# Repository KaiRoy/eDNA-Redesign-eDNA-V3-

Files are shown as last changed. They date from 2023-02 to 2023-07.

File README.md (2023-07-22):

# eDNA Board V3.0 - A Redesign of the OPEnS Lab's eDNA Control Board
A redesign of the Main Control Board for the eDNA Sampler

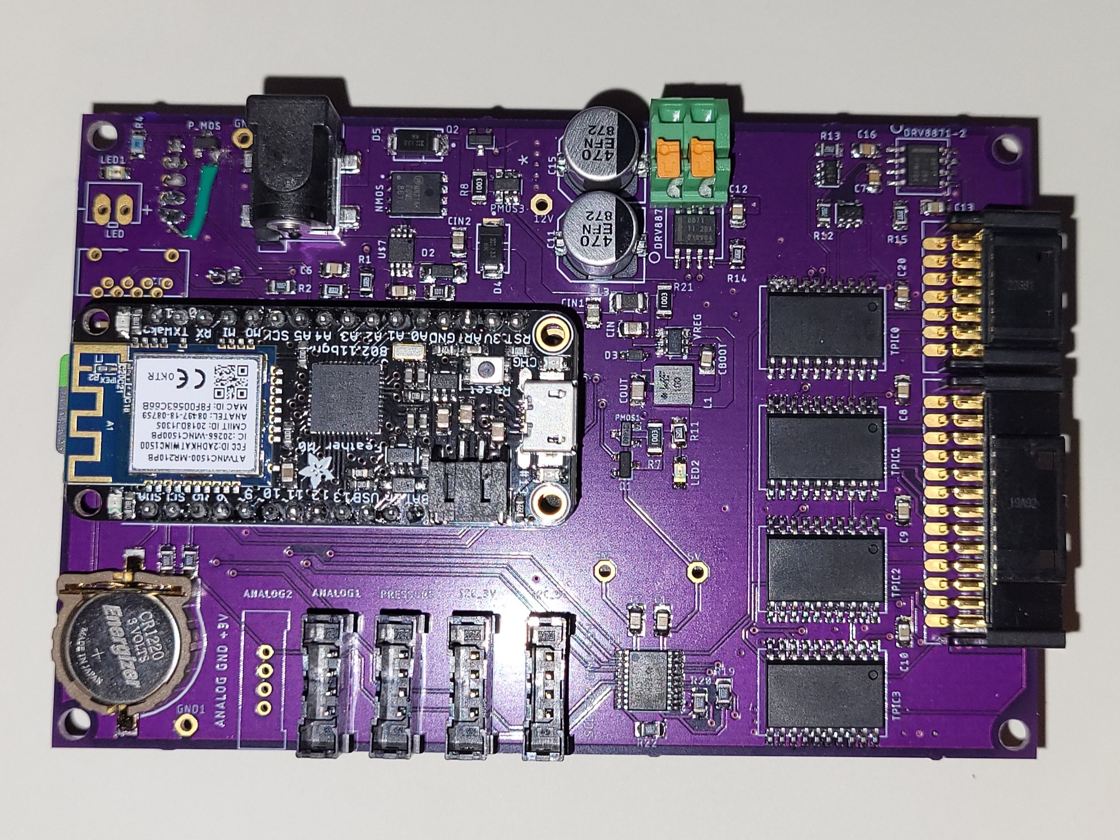
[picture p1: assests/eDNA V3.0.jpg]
Image of an assembled eDNA Board V3.0


## Table of Contents

- [Description](#description)
- [Design](#design)
- [Current State](#current-state-of-the-project)
- [Post Project Notes](#post-project-notes)
- [Installation](#installation) <!-- Should I have Installation and Usage above or below the Design, Current State, Changes, etc? -->
- [Usage](#usage)
- [Credits](#credits)
- [License](#license)

## Description

I have worked on the eDNA project at the OPEnS Lab for the past two years and during that time I noticed a couple of things that I wanted to change about the current electronics board (Dubbed eDNA Electronics V2). Because of other responsiblities, I never had the time to make those changes so I decided to make a Project Course out of it to ensure that I would have the time. This meant I had to limit the number of changes that I wanted to make for time purposes. Here were the goals for the project/redesign:
- Allowing for 5V sensor support (mainly I2C sensor support)
- Redesigning the Power Management Circuits to allow for easier integration of wake-from-sleep interrupts
- Write Documentation for this version and the previous version, since no documentation does not exist

## Designs

Most of the circuits on this board have already been designed and I had no intention of fundamentally changing them in this redesign. The circuits that are being redesigned are the sleep/power management circuit and the logic level converter circuit. The other circuits only get changed on the PCB Layout level, changing as many two-terminal components from 1206 to 0805 and general rearrangement of the PCB Layout.

![Schematic of the Power Management Circuit in eDNA Board V2]()

The power management (PM) system was designed to disable the output of the voltage regulator (Vreg). This would conserve a lot of power as most of the circuits and devices would be powered off, with only the RTC and parts of the PM circuit still functioning. This circuit work by using a D Flip Flop connected to the Microcontroller and the RTC to enable or disable the output of the Vreg Circuit. Because of this design, the microcontroller was completely off with only the RTC Interrupt able to wake up the microcontroller. This makes it difficult to add additional external interrupts to wake the system from sleep. We encountered this problem when we tried to add a button that would wake the system from sleep and trigger an operation.

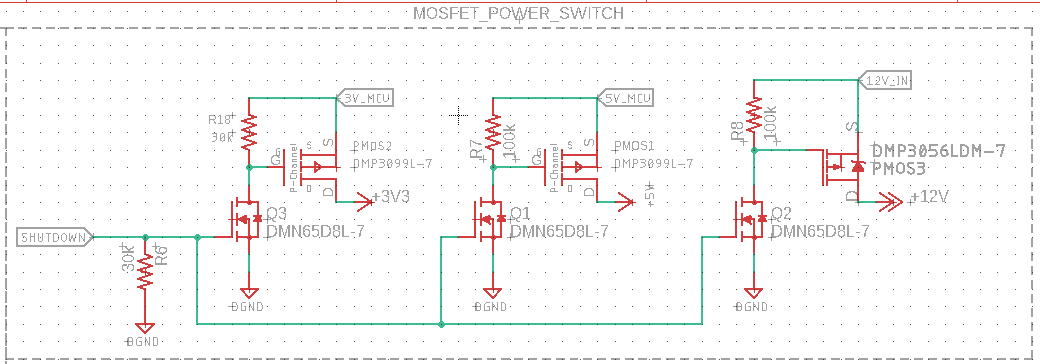
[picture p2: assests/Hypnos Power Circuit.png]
Schematic of the Power Management Circuit in Hypnosv3.4


Another project from the OPEnS Lab created a PM circuit that is used by the majority of projects at the OPEnS Lab, the eDNA project being one of the few projects that do not. This project, called the Hypnos Board, uses a series of MOSFETs to enable and disable power lines going to peripheral devices, leaving the microcontroller powered. We can further conserve power by putting the microctronller into a deep sleep. This will allow us to easily add new wake-from-sleep interrupts while still conserving power.

According to other employees at the OPEnS Lab and some online research the Adafruit Feather M0, the OPEnS Lab's Microcontroller of choice, consumes 1-2mA of current while in a software sleep. Based on the size of the battery, power consumption during operation, and the size of the battery, the approximate current draw while in sleep should be little enough that the sampler can complete a full 24 operations over the course of 30 days, which is what the eDNA Sampler was designed to be able to do. 

The change in the logic level converter circuit was needed because 5V I2C sensor support was desired for the eDNA Sampler. This is because many I2C sensors function off of 5V and limiting the system to only 3.3V I2C sensors can make it difficult to add desired features or functionality. The current logic level converter, a module from Sparkfun, only has 4-channels of conversion with three already in use. Since the circuit needed to be changed anyway, instead of using a module like the one from SparkFun, an IC was found to serve the purpose. The IC used in the v3.0 is the TXS0108E, an eight channel logic level converter.

## Current State of the Project

I was able to do some testing by the end of the term and discovered a couple of mistakes. These mistakes had to do with how I wired certain components up on at the schematic level. I misconnceted the Sleep LED and the RTC_INT Pull-Up Resistor. The sleep LED is less important but rewiring it to my always-on 3.3V line instead of my peripheral device 3.3V line allowed me to better see if the sleep switch/circuit was functioning correctly. The RTC_INT Pull-Up Resistor on the other had was a major error. I had connected the resistor to the Peripheral 3.3V line instead of the always-on 3.3V, meaning that the power would be cut during sleep. Since the RTC_INT is necessary for waking up, this caused a constant cycle of the sleep mode being enabled, the drop in voltage triggering the interrupt, the system waking up, realizing that it has not reached the desired wake-up time, and falling back asleep. 

![Image of an assembled eDNA Board V3.0 with splice wires]()

These mistakes could have been caught if I spent more time at the planning and schematic levels review the design before moving onto the PCB design. Something I plan to allocate time for in future projects. Because of this wiring issues, this version of the board remains untested. There are plans to cut the necessary traces and solder splice wires to reconenct the components and continue testing.

## Post Project Notes

In the future I would spend a lot more time verifying the schematic level of my design to ensure that I have no obvious mistakes, such as the wiring mistakes that I made in the first version of this board. If I am working on a project that is time limited, I would be sure to allocate more than enough time to spend verifying my design/schematic before moving onto the development of the PCB. 

I would also use KiCad over EAGLE in the future if possible. Having used both of the EDA softwares, I have developed a preference towards KiCad over EAGLE due to KiCad's Hotkey and Shortcut based control scheme. This has made my workflows in KiCad feel much smoother to me than my workflows in EAGLE have. In addition, I have been using the free version of EAGLE which has limitations on what can be done in the software, while KiCad does not. 

Below are a list of changes that I would recommend be made in future version of this board. I have split it into two categories as there is a difference between the changes that I would personally like to make, and the changes that I would recommend to the OPEnS Lab. Since the OPEnS Lab cannot simply make changes for the sack of making changes, the changes I recommend are ones that I see having a better Benefit-Cost Ratio conisdering the current state of the Project. 

What I would recommend for the next OPEnS Lab Version:
- Find a new Voltage Regulator IC/Redesign the Vreg Circuit
	- This IC was chosen as it had an Enable pin and its was automotive grade. Since neither of these specifications are that important I would recommend looking into a new IC that is easier to come by, since this one has been very hard to purchase in the past. 
- Redesign the Shift Registers to use the existing SPI Pins on the Feather M0
	- If that is not possible with the current Shift Registers for any reason, I would recommend finiding new Shift Registers to use in the design.

For my own personal version (outside of the OPEnS Lab):
- Switch to an ESP32 based design
	- Deep Sleep Functionality
  	- Built in RTC and WiFi Modules
  	- Similar amount of I/O Pins
	- Larger Program Memory (Our debug code is limited by the size of the Feather M0 Program Memory)
- Redesign the PCB with the intention of purchasing them preassembled. 
	- This would allow for smaller componenets to be used, components too small to be easily assembled by hand. 
	- This would allow for a two-sided PCB design i.e components on either side of the PCB, something that is hard to do by hand.

## Installation

What EDA libraries and files are needed for this project?
- eDNA Library
- Various Component Libraries
<!-- Make a singular Library for all of the components Symbols and footprints -->
<!-- Insert a link to a library guide or make my own -->

<!-- Add a link to the firmware installation guide -->
<!-- Note which code version to use -->

<!--
## Usage

Provide instructions and examples for use. Include screenshots as needed.

To add a screenshot, create an `assets/images` folder in your repository and upload your screenshot to it. Then, using the relative filepath, add it to your README using the following syntax:

    ```md
    ![alt text](assets/images/screenshot.png)
    ```

## Features

If your project has a lot of features, list them here.

## Tests

-->

## Credits

List your collaborators, if any, with links to their GitHub profiles.
- Nathan Jesudason: Modifying the [Sampler Code](https://github.com/OPEnSLab-OSU/ednaServer/tree/54-revamp-sleep-system) Changes for testing

If you used any third-party assets that require attribution, list the creators with links to their primary web presence in this section.
- OPEnS Lab's [Hypnos Board V3.4](https://github.com/OPEnSLab-OSU/OPEnS-Hypnos)
- A branch of the [ednaServer](https://github.com/OPEnSLab-OSU/ednaServer/tree/54-revamp-sleep-system) code
<!-- Link the Symbols and Footprints used? -->

## License

Licensed under the [CERN-OHL-S-2.0](LICENSE.txt) License

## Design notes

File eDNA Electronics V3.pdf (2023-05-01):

# eDNA Electronics V3

By Kai Quintin Kurisaka Roy

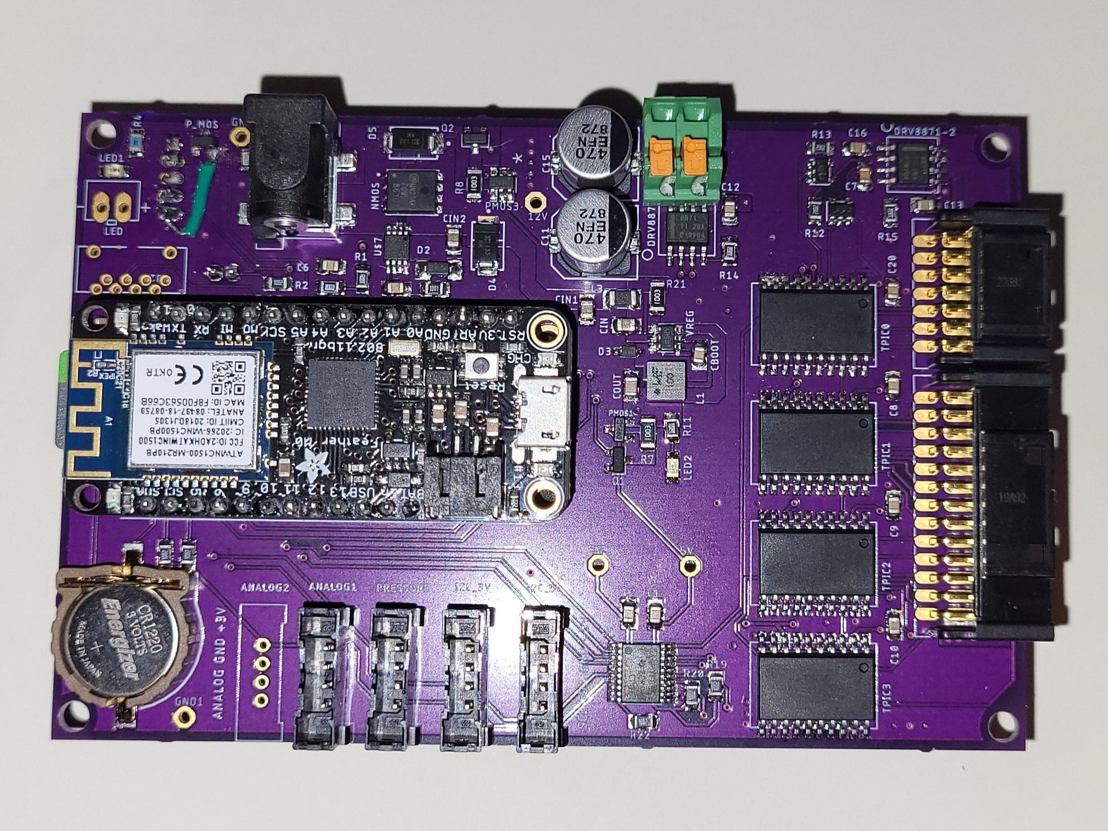
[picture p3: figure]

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
Table of Con

tents

2
Top Le

vel Block Diagrams

2
Whole Circuit Schematics and PCB

2
Micocontroller
- Adafruit

Feather M0 WiFi

2
Pin Usag

e in our Circuit:

4
R

e

verse Curren

t Protection (RCP) Circuit

7
Voltag

e

Regula

tor (VReg) Circuit

9
MOSFET

P

o

wer Control Circuit | 11
Valv
e Control Circuit: | 12
Motor/Ball

Valv

e Control Circuit: | 15
Other/Miscellaneous Circuits | 16
Sleep Mode Control Circuit: | 16
Logic Con
verter: | 18
SD Car
d Circuit: | 18
Connectors: | 18
Notes on

Possible Impr

o

vements: | 19

# Top Level Block Diagrams

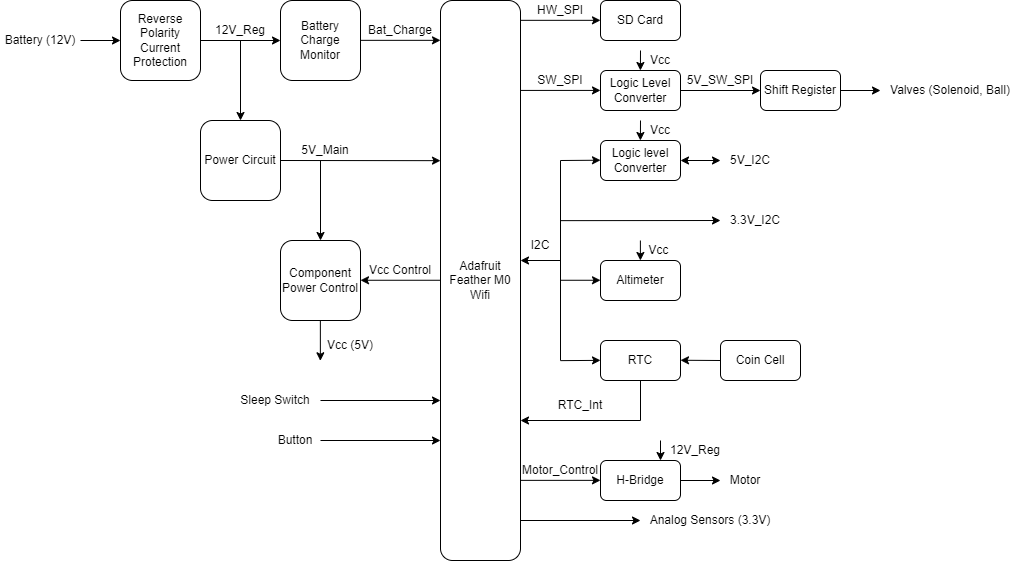
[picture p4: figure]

Figure #: Top-Level Block Diagram

# Whole Circuit Schematics and PCB

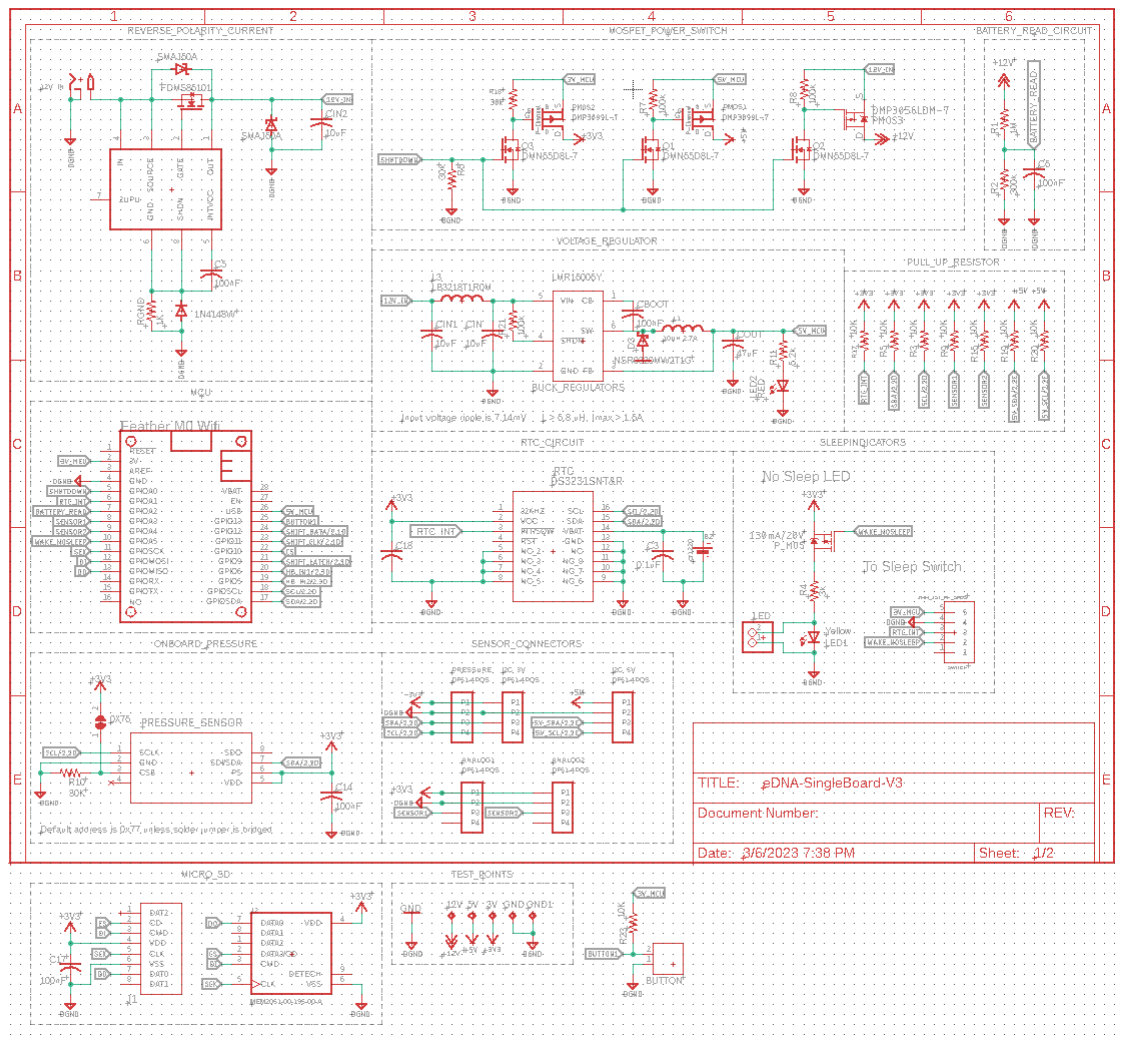
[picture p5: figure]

Figure #: Sheet 1 of the eDNA Board Schematic

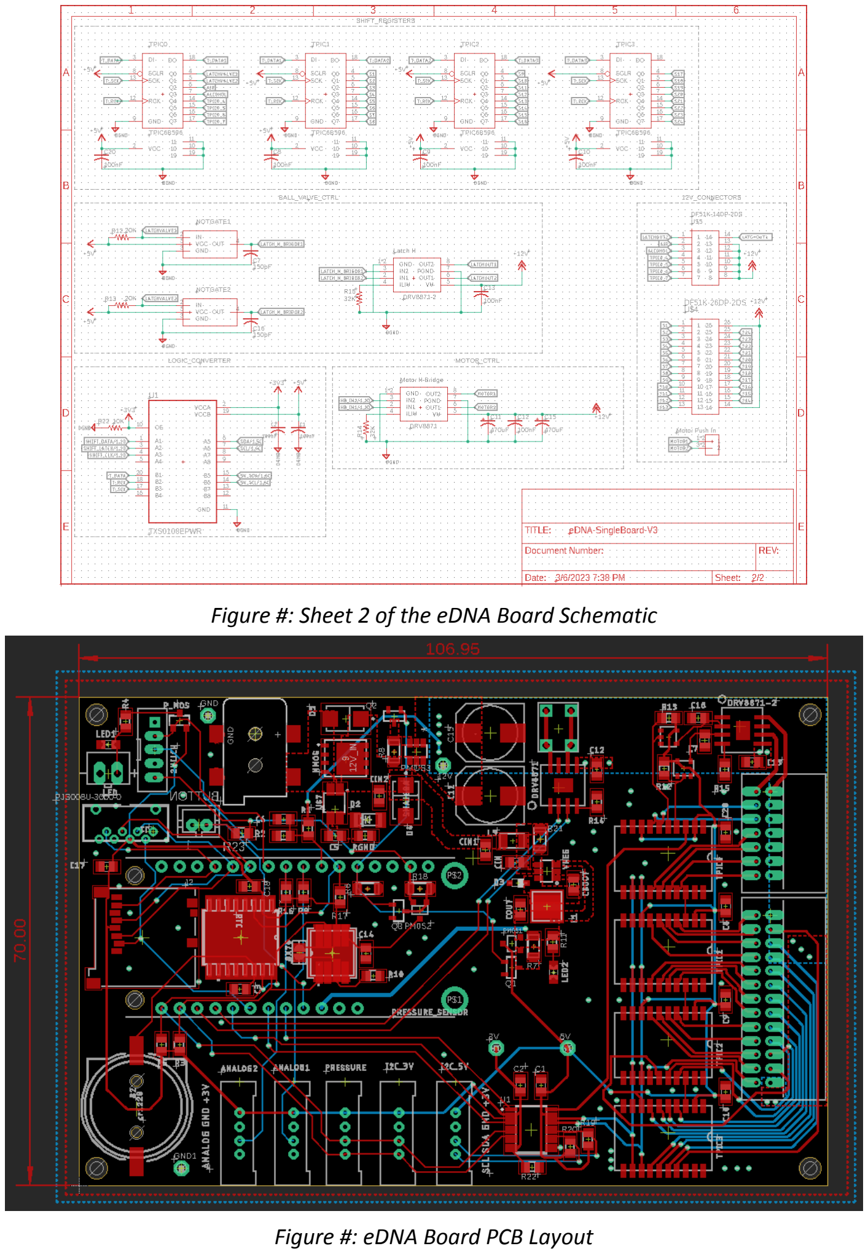
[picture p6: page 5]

Figure #: Sheet 2 of the eDNA Board Schematic

Figure #: eDNA Board PCB Layout

# Micocontroller - Adafruit Feather M0 WiFi

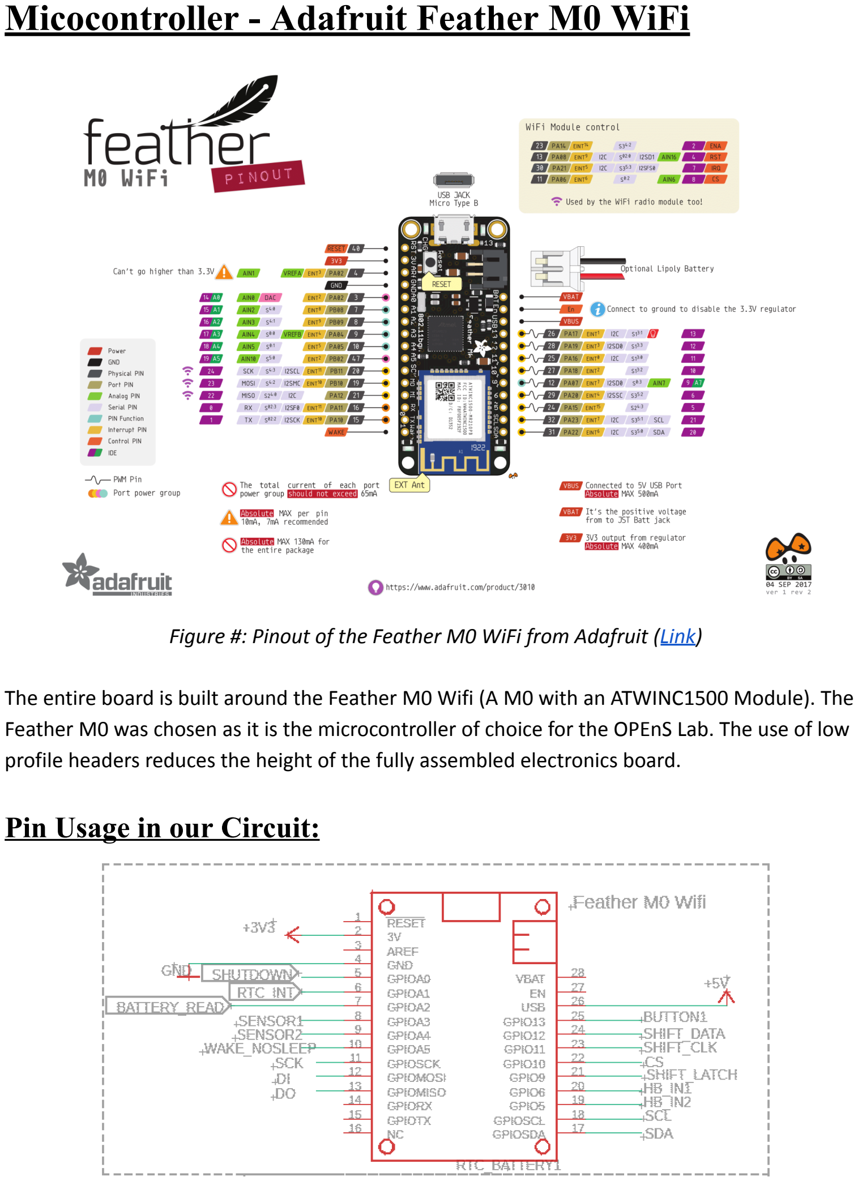
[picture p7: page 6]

Figure #: Pinout of the Feather M0 WiFi from Adafruit (Link) (https://learn.adafruit.com/assets/46250)

The entire board is built around the Feather M0 Wifi (A M0 with an ATWINC1500 Module). The Feather M0 was chosen as it is the microcontroller of choice for the OPEnS Lab. The use of low profile headers reduces the height of the fully assembled electronics board.

## Pin Usage in our Circuit:

- Pins 12, 11, and 9 are used to control the 4 Shift Registers that control the Valves.
- Pin 12 is the Data pin,
- Pin 11 is the Clock(CLK) pin,
- Pin 9 is the Latch Pin.
- Pins A1 and A5 connect to the sleep Circuit. Pin A1 is connected to the RTC Interrupt (RTC_INT on the schematic).
- Pin A5 is used by the Feather in order to determine if it is in wake mode or sleep mode.
- Pins A3 and A4 are used for the 2 Analog Sensors
- Pins SCK, MO, MI, and 10 are used to control the Micro SD Card Reader.
- Pin 10 is the SD Card Readers Chip Select (CS) Pin.
- The other pins are the typical SPI Communication Pins (SLCK, MOSI, MISO).
- Pins 5 and 6 are used to control the motor via the H-Bridge (DRV8871).
- Using two pins allows the feather to run the motor in both directions.
- The H-Bridge allows us to power the motor with 12V while controlling it with the Feather.
- Pin A2 is the Battery Read Pin
- Pin A0 is the Shutdown Pin
- Pin 13 is marked as a button pin but is not connected to anything on the Current PCB Design.
- The 3V and USB pins are connected to 3.3V and 5V lines respectively.
- Pins SCL and SDA are used to control any I

2C device.
- Current I

2C devices include the RTC and the In-Line Pressure Sensor.
- Pins RST, ARf, RX, TX, Wake, Bat, En are not used.

# Reverse Current Protection (RCP) Circuit

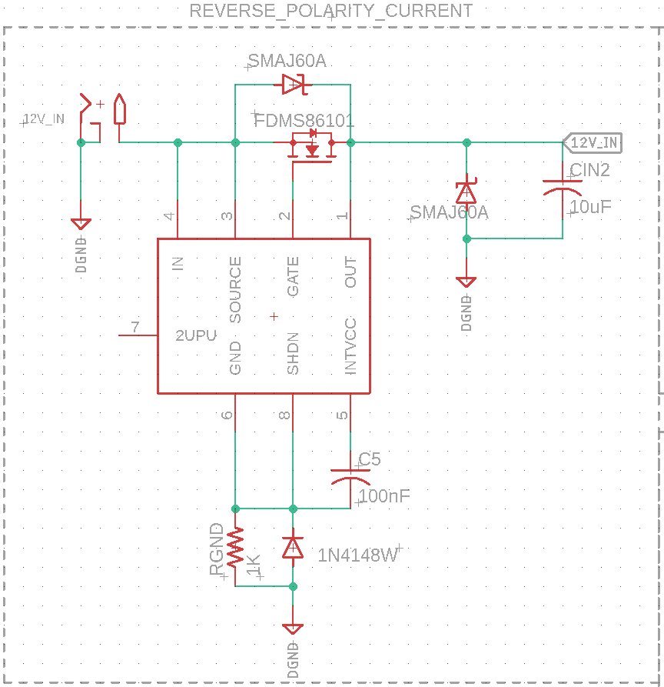
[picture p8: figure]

Figure #: Schematic of the Reverse Current Protection Circuit

This circuit is implemented to protect the battery in case something causes the current to flow towards the power source. While our battery of choice has its own protection circuits, when those circuits are triggered, the battery stops providing power and needs to be reset with the charger. By having this circuit in place, we can prevent any reverse current and prevent the battery from shutting off unexpectedly.

The integrated circuit used for this circuit is the LTC4372 Ideal Diode Controller. The supporting circuit was taken from page 18 of the LTC4372 Datasheet, specifically the left half of Figure 15, “Micropower 12V Surge Stopper with Ideal Diode.”

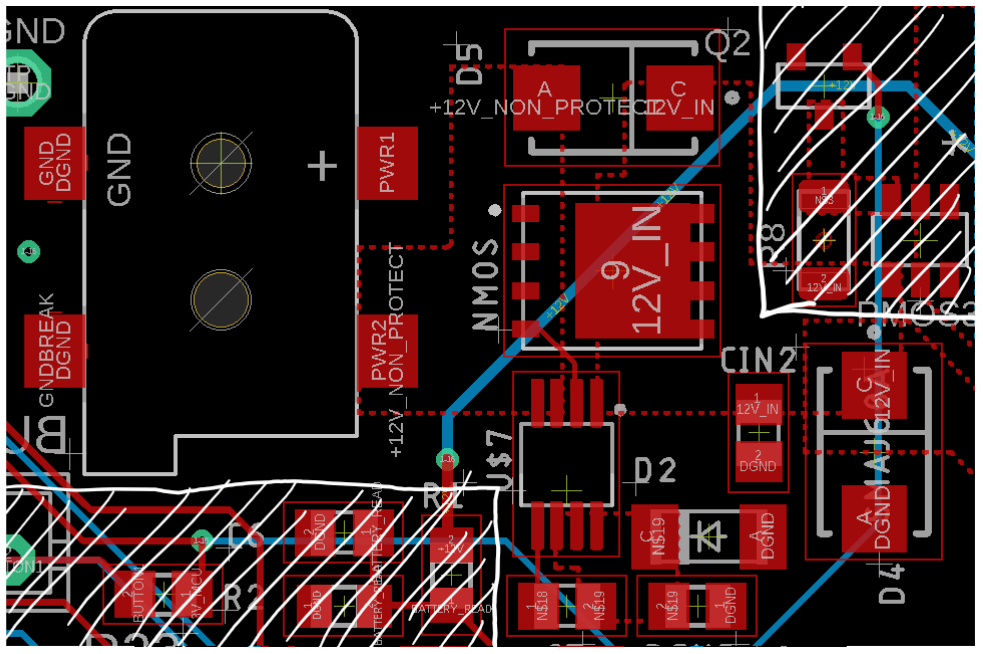
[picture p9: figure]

Figure #: PCB Layout of the Reverse Current Protection Circuit

The components were layed out so that the small copper plans could be used to connect the different components together. This is allows for both a high amount of current to flow through the plane, as well as assist with heat dissipation of the components. There is a “12V_Non_Protect” plane that connects the 12V input connector with the Protection IC and the supporting components. The output of the IC is the “12V_IN” plane which later connects to both the Mosfet Power Control Circuit and the 5V Buck Converter Circuit.

The 0805 package was used for most of the 2 terminal devices (capacitors, resistors, etc.) to reduce the overall size of the layout while maintaining the ability for the board to be assembled by hand. In many cases, any non-0805 component is chosen because of a lack of a 0805 version of that device. *Components that face higher currents and voltages typically need to be larger to handle the higher load.*

The marked out area in the top right corner of the image contains some of the components for the Mosfet Power Control circuit, specifically the components needed for the 12V/High Power Rail. This circuit will be discussed later in this report.

# Voltage Regulator (VReg) Circuit

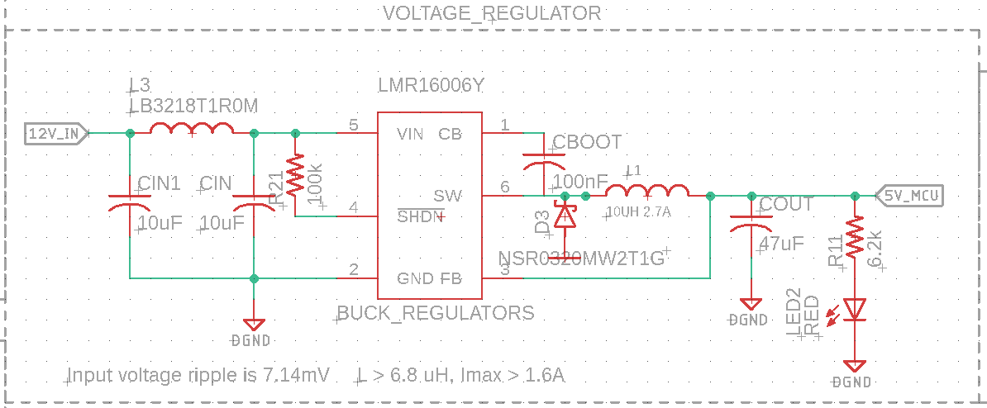
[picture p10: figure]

Figure #: Schematic of the Voltage Regulator Circuit

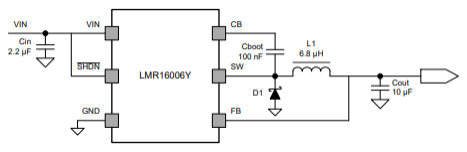
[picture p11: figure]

Figure #: Manufacture recommended schematic for the LMR16006YQ5. Page X of the datasheet.

Since a 12V battery is used to power all of the electromechanical devices in the eDNA sampler, this input voltage needs to be reduced to 5V and 3.3V for all of the logic components used in the board. Since the Feather M0 has a 5V-to-3.3V regulator built-in to the board, we only need to handle the 12V to 5V conversion.

The LMR16006YQ5 was chosen as it is a Buck Regulator. The buck regulator aspect of the IC is useful for any fluctuations in voltage caused by the electromechanical devices of the eDNA system as the IC uses a feedback pin to maintain the stable 5V output.

An additional LC filter was added to the input of the LMR16006YQ5 to further reduce the noise that comes out of the IC’s output. A resistor and LED combo was also added as an indicator of the Voltage Regulator functioning. Other deviations from the recommended layout include:
- The CIN1 capacitor changed from 2.2uF to 10uF.
- The L1

inductor changed from 6.8uH to 10uH.
- The Cout capacitor changed from 10uF to 47uF.

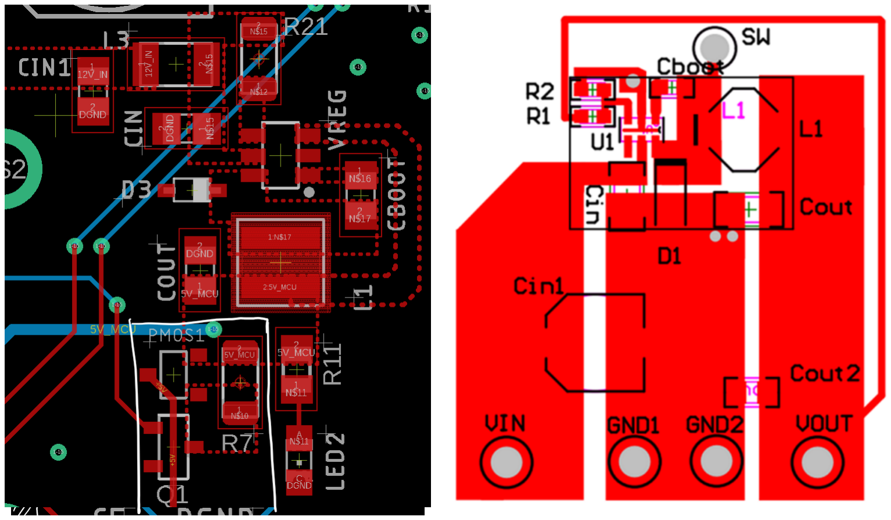
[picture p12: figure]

Figure # (Left): PCB Layout of the Voltage Regulator Circuit
Figure # (Right): Manufacture recommended layout for the LMR16006Y IC.

The PCB Layout was designed to follow a similar layout to the one recommended by the manufacturer with some modifications to accommodate the additional components. The Circuit was also placed as close to the RCP Circuit to reduce the overall size of the “12V_IN” copper plane/trace.

The components outlined in white are for the Mosfet Power Control Circuit which will be covered later in the report. Specifically these are the mosfets used to control the 5V rail for all of the peripheral devices.

# MOSFET Power Control Circuit

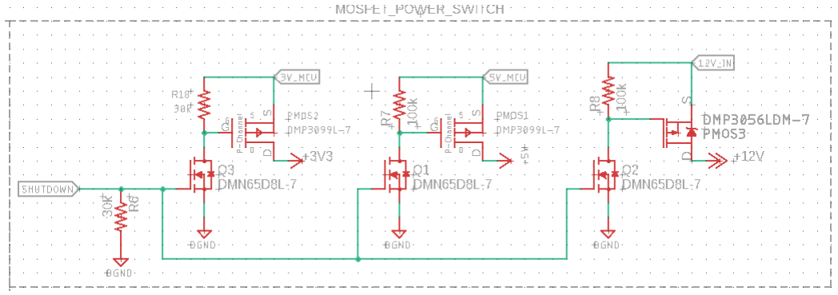
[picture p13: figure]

Figure #: Schematic of the MOSFET Power Control Circuit

The MOSFET Power Control (MPC) Circuit is designed to replace the old D-Flip-Flop (DFF) based power management/saving circuit. The DFF based circuit was designed to shut down the voltage regulator cutting 5V power. This meant that the only things being powered in the circuit were the DFF circuit, Voltage Regulator (even though it was not providing power) and the RTC circuit, which had its own battery. This meant that the Microcontroller was completely powered off which made the system unable to wake up from an interrupt, at least normally. The RTC interrupt had to be connected to the DFF Circuit to turn the Voltage Regulator back on, thus powering the Microcontroller.

The MPC Circuit is based off of the one used in the Hypnos Board, which is designed to use the Microcontroller’s sleep system and simply cutoff power to any peripheral devices; anything that does not used to wake up the feather. The only modification made was to the 3.3V Rail MOSFET circuit. In the Hypnos design, this was controlled separately from the 5V and HighPower MOSFET circuits. Since the eDNA circuit only has one available pin for Power Control, the 5V circuit was replicated for the 3.3V Rail and connected to the same control pin.

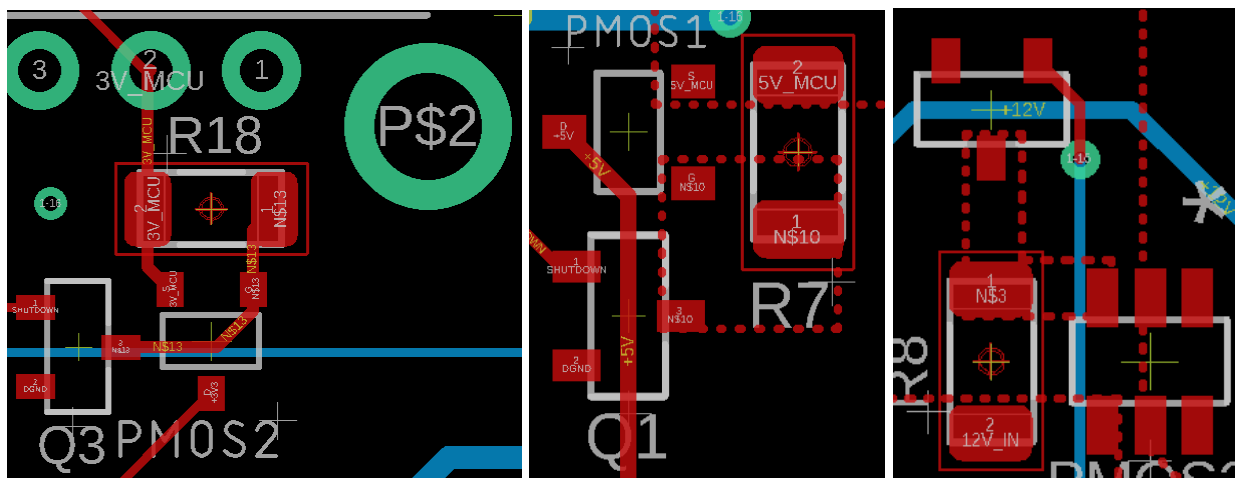
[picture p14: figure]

Figures #, #, #: PCB Layouts for the MOSFET Power Control Circuit

For the layout of the MPC Circuits, the circuit was separated into the 3.3V, 5V, and High Power (12V) sets of components. Each set was placed as close to their respective power supplies as possible. The 12V MPC was placed next to the RCP Circuit, the 5V MPC was placed next to the VReg Circuit, and the 3V MPC was placed right next to the 3V Pin/Head of the Microcontroller.

# Valve Control Circuit:

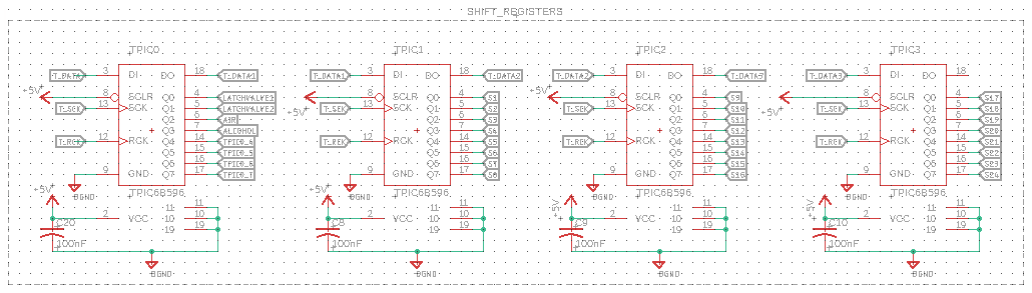
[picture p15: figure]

Figure #: Schematic for the Valve Control/Shift Register Circuit

The Valve Control Circuitry controls the activation of the 24 sampling valves as well as most of the central components. The motor is the only output device that is not controlled by this circuitry. There are four total Shift Registers (TPIC), one to control the central components and three to control the sampling valves.

The Valve Control Circuitry is controlled by the Feather via three signals: Data, Latch, and Clock. These signals go through the logic level converter to convert the 3.3V signal from the Feather into a 5V signal that is used by the TPICs. The Clock and Latch signals are connected to the TPICs in parallel, while the Data signal is connected to the TPICs in series (i.e TPIC0’s Data_In is connected to the logic level shifter data output, TPIC0’s Data_Out is connected to TPIC1’s Data_In and so on). The TPICs communicate in a way very similar to SPI with a data, clock and cs pin (the latch pin). While it should be possible to connect these TPICs to the hardware SPI pins on the microcontrolller, the previous electrical had difficulty getting both the WiFi and TPICs working simultaneously with the TPICs connected to the Hardware SPI pins.

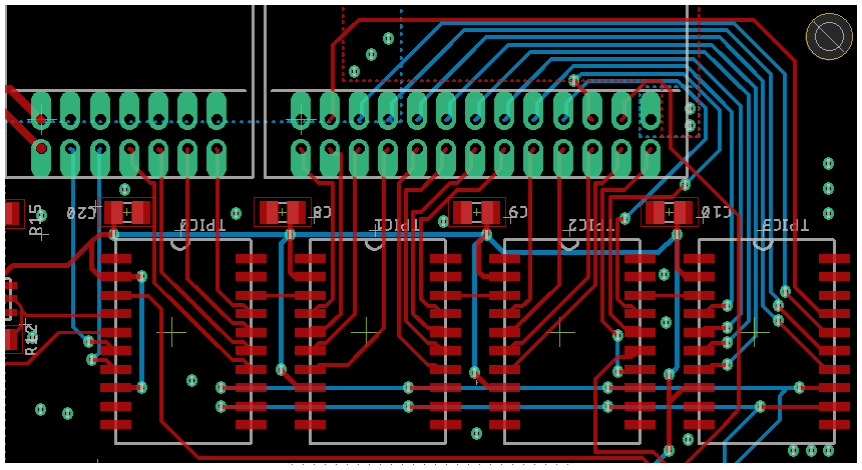
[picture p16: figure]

Figure #: PCB for the Valve Control/Shift Register Circuit

The TPICs are placed near the relevant connectors to keep the traces compact. To the left of the image is where the additional circuitry for the Ball Valve is located. I attempted to keep the circuit relatively compact but since I was keeping the overall board footprint the same size, there is a lot of extra unused space. The traces between the connector and the TPICs are slightly thicker than the rest of the circuit as these traces will have more current running through them as they serve as the drain for the 12V Valves.

# Motor/Ball Valve Control Circuit:

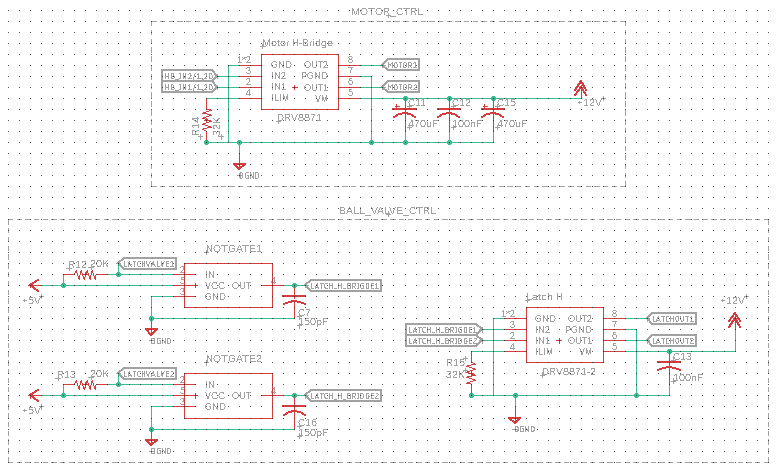
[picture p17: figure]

Figure #: Schematics for the Motor and Ball Valve Circuits

While most of the TPIC Outputs connect directly to the connectors, the two signals for the Ball Valve, LatchValve1 and LatchValve2, go through additional circuitry (right image) before connecting to the connectors. Like with the motor, the ball valve needs to be controlled by an H-Bridge. Since the TPICs pull the output lines to ground, the signal for the Ball valve needs to be inverted before entering the H-Bridge.

An H-Bridge (DRV8871) is used to control the motor in the eDNA Sampler. An H-bridge is used as it allows for the motor to be run at 4 modes of operation (Forward, Backwards, Coast, Break) at 12V. The circuit used in the eDNA Circuit is the same circuit that can be found on page 7 of the DRV8871 Datasheet. The two 470uF Capacitors function as the bulk capacitor
recommended in the data sheet. The 32k ohm value for the resistor was chosen to reduce the motor current to 2A. The calculation for this resistor value can be found on page 9 of the DRV8871 Datasheet.

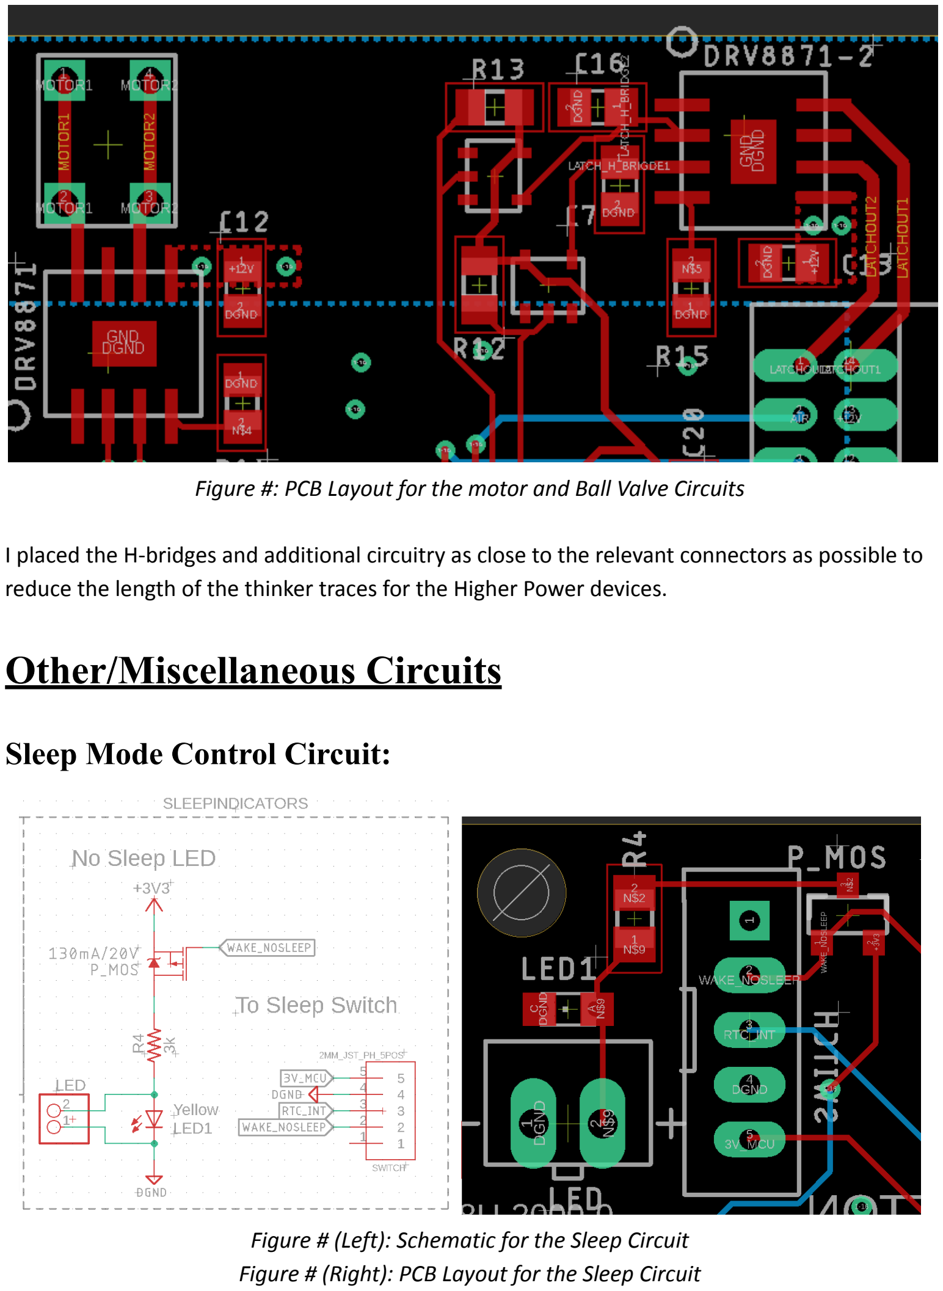
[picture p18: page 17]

Figure #: PCB Layout for the motor and Ball Valve Circuits

I placed the H-bridges and additional circuitry as close to the relevant connectors as possible to reduce the length of the thinker traces for the Higher Power devices.

# Other/Miscellaneous Circuits

## Sleep Mode Control Circuit:

Figure # (Left): Schematic for the Sleep Circuit Figure # (Right): PCB Layout for the Sleep Circuit

The image on the right shows two different circuits: The Switch Connector on the left and the No Sleep Indicator Circuit on the right. The Switch Connector connects to a DPDT toggle switch which is used to enable or disable sleep functionality.

The No Sleep Indicator Circuit is used to indicate whether the Sampler is in No Sleep Mode or not. When in No Sleep Mode, the Yellow LED will Light Up. There is also a connection point where an external LED can be attached if it is desired to have the sleep indicator LED outside of the electronics box.

## Logic Converter:

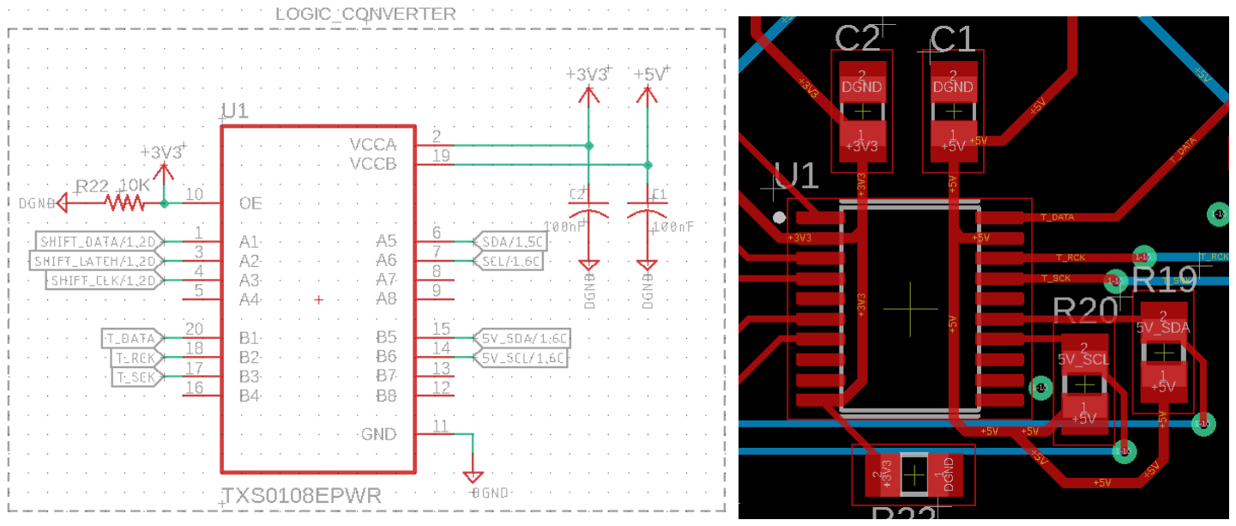
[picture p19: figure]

Figure # (Left): Schematic for the Logic Converter Circuit Figure # (Right): PCB Layout for the Logic Converter Circuit

The logic level converter circuit allows for the conversion of 3.3V digital signals to 5V signals. This is important since the microcontroller functions on 3.3V logic. The logic converter IC being used is the TXS0108E, an 8-channel Logic Level Converter IC. Three of these Channels are used for the Shift Register (TPIC) circuit, while 2 others are used to allow for 5V I2C capability. Like with many other circuits on this board, this circuit simply follows the recommended layout outlined in the IC’s datasheet.

## SD Card Circuit:

The SD Card is set up using the SPI Communication protocol. The 0.1uF capacitor acts as a decoupling capacitor. Outside of that the circuit set up is straightforward.

## Connectors:

Three connectors are used for any external I2C device, one of which is used by the in-line pressure sensor. This allows for 2 more I2C sensors to be added to the machine before the logic board will have to be redesigned. For the I2C protocol to function correctly, the SDA and SCL lines need to be pulled up to 5Vs. Two resistors are used for this purpose.

There are two connectors/pins allocated for analog sensors, one of which is already in use for the flow sensor. The other connector is used in the SampleNow implementation for the SampleNow Button. If more than one analog sensor needs to be added then the board will need to be redesigned. It is recommended that you try to find an I2C version for any sensor that needs to be added.

# Notes on Possible Improvements:

- Changing to a Hardware SPI instead of Software SPI for Shift Registers
- This would allow for:
- The use of the SPI Library in the Code
- The freeing of 2 digital pins on the Feather.
- Idea by Kai
- Splitting the 26-Pin Connector into two 14-Pins Connectors
- This would allow each side (set of 12 valves) to have its own connector
- Idea by Kai.
- Add a reset button connected to the reset pin
- Idea by Kai
- Changing the SD Card Holder
- Current one is a Push In, Push Out style Holder which is hard to use with the current Electronics box
- The Space between where the SD card comes out and the wall of the box is tight
- Change with a top latching holder or a vertical holder
- Top Latching is not recommended as the seem to be less reliable
- Suggested by Kai
- Embedding the micro controller into the PCB
- More fine control of the MCU and Pins
- No need for headers, reduces overall Board Height
- Pro/Con: Depending on whether the board is designed for Pre-Assembly, could increase the size of the board as components can not be “placed under the Feather”.
- Suggested by Kai
- Order the boards pre-assembled/machine assembled
- Currently employees assemble the boards by hand, which limits the minimum size of components as well as keeping the board single sided
- Buying Pre-Assembled Boards could allow the following
- Using smaller SMD components, saving space
- Allow for components on each side, further saving space
- Higher consistency, i.e little human error in assembly
- Con: Increased cost (double side will increase components even more
- Switch to a SPST Switch with a 3-pin connector on the board
- RTC_INT pin is no longer needed on the switch as the sleep control circuit is different

- Switch to an external uSD Card Slot (Waterproof)
- Allows for easy user access to the uSD Card
- Would need a connector on the board to connect.
- Suggested by Kai
- Change the Valve Connectors to better fit the PCB Layout OR Change the layout to better fit the connectors.
- As it currently stands, the first Shift Register (TPIC0) is the furthest TPIC away from the logic converter, this is mostly due to the location of the power circuits which need to sit on the top right of the board (at least in this design). By switching the central valve connector with the sample valve connector(s), you switch the TPIC placement so that TPIC0 sits closer to the logic converter
- NOTE: This poin may be moot as new Shift Registers will need to be found as these ones are either discontinued/non-stocked or very hard to come by.
- Would also recommend finding smaller footprint device(s) if the board is switched to a Pre-Assembly Design.
- Move any indicator LEDs to be power off of the Peripheral Rail
- I (Kai) forgot to switch the VReg LED to be power off of the Post-MPC Power Rails.

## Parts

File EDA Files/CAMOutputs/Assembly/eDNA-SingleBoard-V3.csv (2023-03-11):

Comment | Designator | Footprint
 | 0X76 | SJ
TPPAD1-13 | 3V | P1-13
TPPAD1-13 | 5V | P1-13
TPPAD1-13 | 12V | P1-13
2.1MMJACKSMT | 12V_IN | DCJACK_2MM_SMT
DF51-4POS | ANALOG1 | DF51-4POS
DF51-4POS | ANALOG2 | DF51-4POS
cr1220 | B2 | CR1220-2
 | BUTTON | JST-PH2
100nF | C1 | C0805
100nF | C2 | C0805
0.1uF | C3 | C0805
100nF | C5 | C0805
100nF | C6 | C0805
150pF | C7 | C0805
100nF | C8 | C0805
100nF | C9 | C0805
100nF | C10 | C0805
470uF | C11 | 140CLH-0810
100nF | C12 | C0805
100nF | C13 | C0805
100nF | C14 | C0805
470uF | C15 | 140CLH-0810
150pF | C16 | C0805
100nF | C17 | C0805
100nF | C18 | C0805
100nF | C20 | C0805
100nF | CBOOT | C0805
10uF | CIN | C0805
10uF | CIN1 | C0805
10uF | CIN2 | C0805
47uF | COUT | C0805
1N4148W | D2 | SOD-123_MINI-SMA
NSR0320MW2T1G | D3 | SOD323_ST
SMAJ60A | D4 | DO_214
SMAJ60A | D5 | DO_214
Motor H-Bridge | DRV8871 | SOP8
Latch H | DRV8871-2 | SOP8
TPPAD1-13 | GND | P1-13
TPPAD1-13 | GND1 | P1-13
DF51-4POS | I2C_3V | DF51-4POS
DF51-4POS | I2C_5V | DF51-4POS
PJS008U-3000-0 | J1 | CONN_PJS008U-3000-0_YAM
MEM2051-00-195-00-A | J2 | GCT_MEM2051-00-195-00-A
10UH 2.7A | L1 | WE-MAPI_40XX
LB3218T1R0M | L3 | INDC3218X200N
2.5MM_JST_UP_2POS | LED | JST_2POS_2.5MM_UP
Yellow | LED1 | CHIPLED_0805
RED | LED2 | CHIPLED_0805
FEATHERWING | MS1 | FEATHERWING
FDMS86101 | NMOS | 8-POWERTDFN
 | NOTGATE1 | SOT753
 | NOTGATE2 | SOT753
DMP3099L-7 | PMOS1 | SOT-23-3
DMP3099L-7 | PMOS2 | SOT-23-3
DMP3056LDM-7 | PMOS3 | SOT23-6
DF51-4POS | PRESSURE | DF51-4POS
MS580302BA01-00 | PRESSURE_SENSOR | MS5803-02BA01
130mA/20V | P_MOS | SOT23-3
DMN65D8L-7 | Q1 | SOT23-S
DMN65D8L-7 | Q2 | SOT23-S
DMN65D8L-7 | Q3 | SOT23-S
1M | R1 | R0805
300k | R2 | R0805
10K | R3 | R0805
3k | R4 | R0805
10K | R5 | R0805
30k | R6 | RES_1206
100k | R7 | RES_1206
100k | R8 | RES_1206
10K | R9 | R0805
30K | R10 | R0805
6.2k | R11 | R0805
20K | R12 | R0805
20K | R13 | R0805
32K | R14 | R0805
32K | R15 | R0805
10K | R16 | R0805
10K | R17 | R0805
30k | R18 | RES_1206
10K | R19 | R0805
10K | R20 | R0805
100k | R21 | RES_1206
10K | R22 | R0805
10K | R23 | R0805
1K | RGND | R0805
DS3231SNT&R | RTC | 21-0042B_16
2MM_JST_PH_5POS | SWITCH | 2MM_5POS_HEADER
TPIC6B596 | TPIC0 | DIP20
TPIC6B596 | TPIC1 | DIP20
TPIC6B596 | TPIC2 | DIP20
TPIC6B596 | TPIC3 | DIP20
Motor Push In | U$2 | 3.5MM_DIP2
DF51K-26DP-2DS | U$4 | DF51K-26DP-2DS-ANGLE
DF51K-14DP-2DS | U$5 | DF51K-14DP-2DS-ANGLE
LTC4372 | U$7 | SOP65P640X120-8N
TXS0108EPWR | U1 | SOP65P640X120-20N
BUCK_REGULATORS | VREG | SOT23-6@1

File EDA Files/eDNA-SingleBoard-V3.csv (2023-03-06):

Qty | Value | Device | Package | Parts | Description | Column1 | _1
1 |  | SJ | SJ | 0X76 | SMD solder JUMPER
1 | 2.1MMJACKSMT | 2.1MMJACKSMT | DCJACK_2MM_SMT | 12V_IN | 2.1mm x 5.5mm THM DC jack with internal switch. Digikey part #PJ-102A, 4UCON part #05537
5 | TPPAD1-13 | TPPAD1-13 | P1-13 | 3V, 5V, 12V, GND, GND1 | Test pad
5 | DF51-4POS | DF51-4POS | DF51-4POS | ANALOG1, ANALOG2, I2C_3V, I2C_5V, PRESSURE
1 | cr1220 | BATTERYCR1220_2 | CR1220-2 | B2 | CR1220 SMT - Digikey: 3001K-ND
1 |  | JST-PH2 | JST-PH2 | BUTTON
14 | 100nF | C-USC0805 | C0805 | C1, C2, C5, C6, C8, C9, C10, C12, C13, C14, C17, C18, C20, CBOOT | CAPACITOR, American symbol
2 | 470uF | CPOL-US140CLH-0810 | 140CLH-0810 | C11, C15 | POLARIZED CAPACITOR, American symbol
1 | 0.1uF | C-USC0805 | C0805 | C3 | CAPACITOR, American symbol
2 | 150pF | C-USC0805 | C0805 | C7, C16 | CAPACITOR, American symbol
3 | 10uF | C-USC0805 | C0805 | CIN, CIN1, CIN2 | CAPACITOR, American symbol
1 | 47uF | C-USC0805 | C0805 | COUT | CAPACITOR, American symbol
1 | 1N4148W | 1N4148W | SOD-123_MINI-SMA | D2
1 | NSR0320MW2T1G | BAT60J | SOD323_ST | D3 | Schottky barrier diode
2 | SMAJ60A | SMAJ60A | DO_214 | D4, D5
1 | Motor H-Bridge | DRV8871 | SOP8 | DRV8871
1 | Latch H | DRV8871 | SOP8 | DRV8871-2
1 | PJS008U-3000-0 | PJS008U-3000-0 | CONN_PJS008U-3000-0_YAM | J1
1 | MEM2051-00-195-00-A | MEM2051-00-195-00-A | GCT_MEM2051-00-195-00-A | J2 | Connector, Memory Card, Micro Sd, 8 Position, 1.1mm, Full Reel Check availability
1 | 10UH 2.7A | WE-MAPI_4030_74438357100 | WE-MAPI_40XX | L1 | SMD Metal Alloy Power Inductor
1 | LB3218T1R0M | LB3218T1R0M | INDC3218X200N | L3 | INDUCTOR, 1µH, 1.075A, ±20%; Inductance:1µH; Inductance Tolerance:± 20%; DC Resistance Max:60mohm; DC Current Rating:1.075A; Self Resonant Frequency:100MHz; Series:LB; Core Material:Ferrite; Inductor Case Style:SMD; No. of Pins:2 ;RoHS Compliant: No
1 | 2.5MM_JST_UP_2POS | 2.5MM_JST_UP_2POS | JST_2POS_2.5MM_UP | LED
1 | Yellow | LEDCHIPLED_0805 | CHIPLED_0805 | LED1 | LED
1 | RED | LEDCHIPLED_0805 | CHIPLED_0805 | LED2 | LED
1 | FEATHERWING | FEATHERWING | FEATHERWING | MS1
1 | FDMS86101 | FDMS86101 | 8-POWERTDFN | NMOS
2 |  | NOT_GATE | SOT753 | NOTGATE1, NOTGATE2
1 | 130mA/20V | MOSFET_PCH-IRLML2244 | SOT23-3 | P_MOS | P-channel MOSFETs
2 | DMP3099L-7 | SSM3J3228R | SOT-23-3 | PMOS1, PMOS2 | PMOS 3.8A (Ta) 1.08W (Ta) Surface Mount SOT-23, 3 pins
1 | DMP3056LDM-7 | P-MOSFET | SOT23-6 | PMOS3 | P-Channel 30V 4.3A (Ta) 1.25W (Ta) Surface Mount SOT-26, 6 pins
1 | MS580302BA01-00 | MS580302BA01-00 | MS5803-02BA01 | PRESSURE_SENSOR | Pressure sensor
3 | DMN65D8L-7 | NMOS | SOT23-S | Q1, Q2, Q3 | N-Channel 310mA (Ta) 370mW (Ta) Surface Mount SOT-23, 3 pins
1 | 1M | R-US_R0805 | R0805 | R1 | RESISTOR, American symbol
1 | 30K | R-US_R0805 | R0805 | R10 | RESISTOR, American symbol
1 | 6.2k | R-US_R0805 | R0805 | R11 | RESISTOR, American symbol
2 | 20K | R-US_R0805 | R0805 | R12, R13 | RESISTOR, American symbol
2 | 32K | R-US_R0805 | R0805 | R14, R15 | RESISTOR, American symbol
1 | 300k | R-US_R0805 | R0805 | R2 | RESISTOR, American symbol
9 | 10K | R-US_R0805 | R0805 | R3, R5, R9, R16, R17, R19, R20, R22, R23 | RESISTOR, American symbol
1 | 3k | R-US_R0805 | R0805 | R4 | RESISTOR, American symbol
2 | 30k | WSLP1206R0500FEA | RES_1206 | R6, R18 | RES 0.05 OHM 1% 1W 1206
3 | 100k | WSLP1206R0500FEA | RES_1206 | R7, R8, R21 | RES 0.05 OHM 1% 1W 1206
1 | 1K | R-US_R0805 | R0805 | RGND | RESISTOR, American symbol
1 | DS3231SNT&R | DS3231SNT&R | 21-0042B_16 | RTC | Real-time clock, RTC, DS3231
1 | 2MM_JST_PH_5POS | 2MM_JST_PH_5POS | 2MM_5POS_HEADER | SWITCH | 5POS JST female, 5 position
4 | TPIC6B596 | TPIC6B596 | DIP20 | TPIC0, TPIC1, TPIC2, TPIC3
1 | Motor Push In | PUSH_IN_2 | 3.5MM_DIP2 | U$2 | Push in to connect
1 | DF51K-26DP-2DS | DF51K-26DP-2DS | DF51K-26DP-2DS-ANGLE | U$4
1 | DF51K-14DP-2DS | DF51K-14DP-2DS | DF51K-14DP-2DS-ANGLE | U$5
1 | LTC4372 | LTC4372 | SOP65P640X120-8N | U$7
1 | TXS0108EPWR | TXS0108EPWR | SOP65P640X120-20N | U1 | Check availability
1 | BUCK_REGULATORS | BUCK_REGULATORS | SOT23-6@1 | VREG

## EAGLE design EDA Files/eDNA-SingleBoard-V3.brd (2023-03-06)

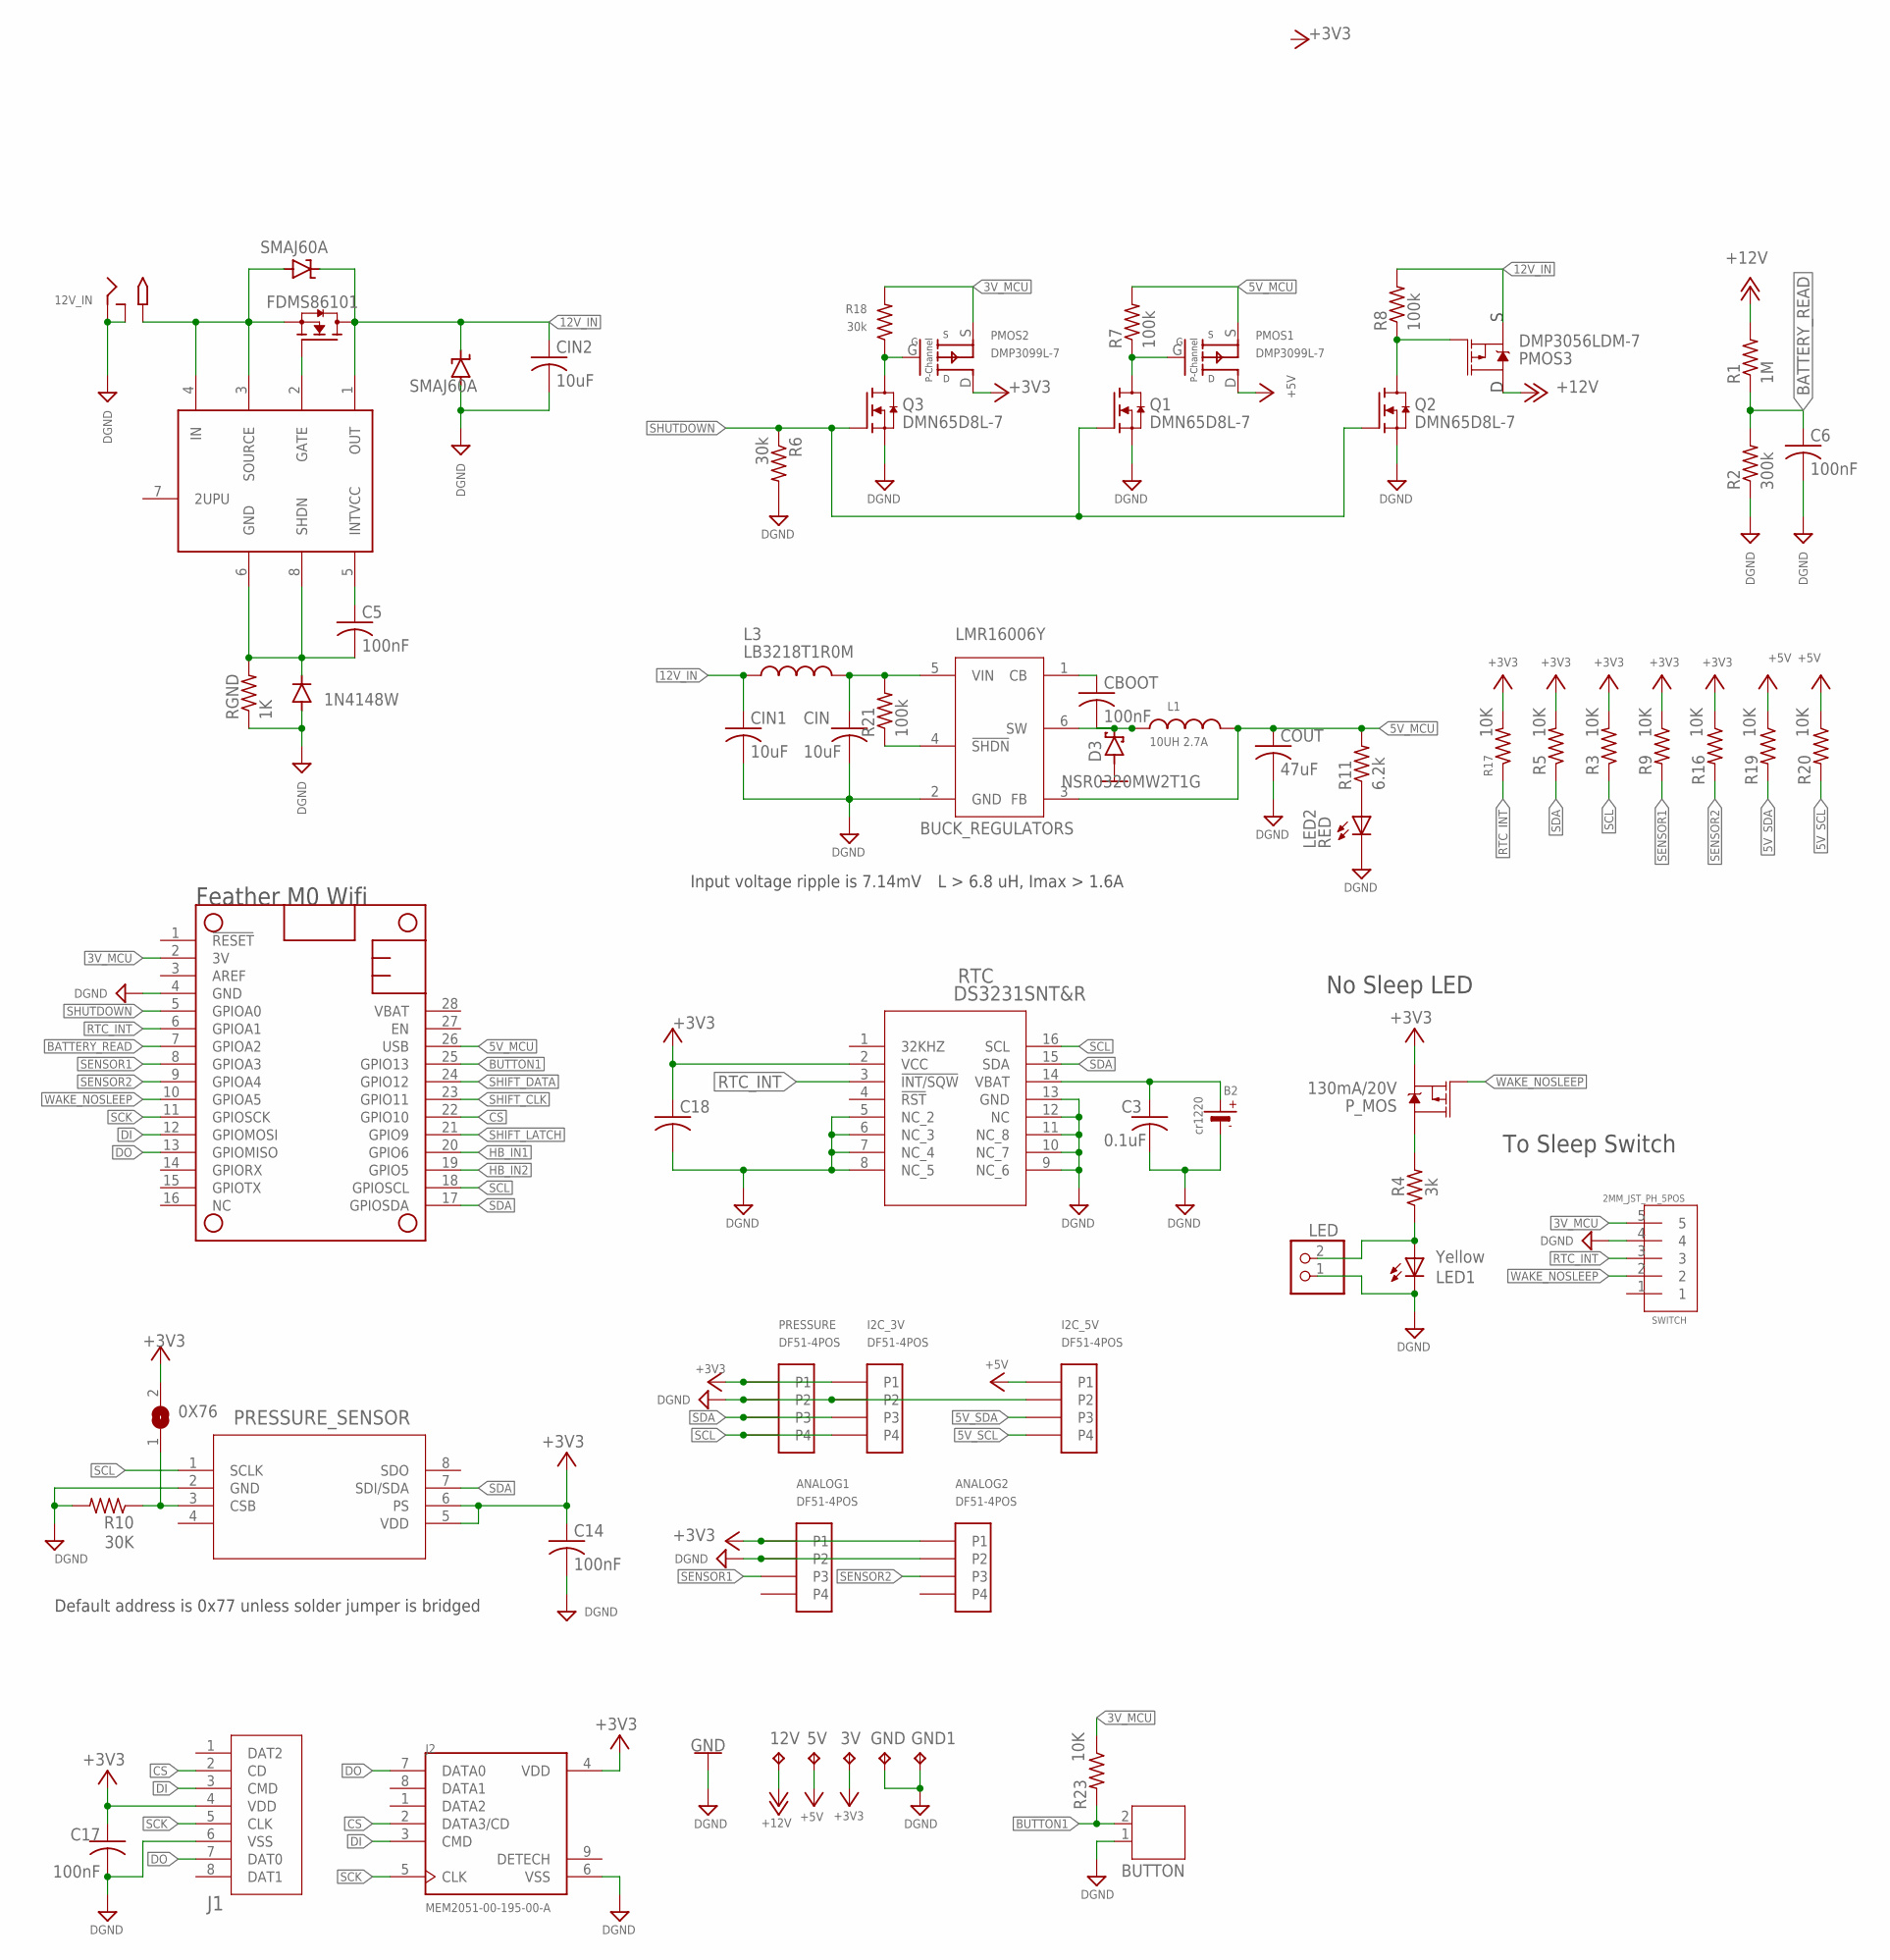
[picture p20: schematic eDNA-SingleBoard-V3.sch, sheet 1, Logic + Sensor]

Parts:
0X76: SJ
3V, 5V, 12V: TPPAD1-13; P1-13
12V_IN: 2.1MMJACKSMT; DCJACK_2MM_SMT
ANALOG1, ANALOG2: DF51-4POS
B2: cr1220; CR1220-2
BUTTON: JST-PH2
C3: 0.1uF; C0805
C5, C6, C14, C17, C18: 100nF; C0805
CBOOT: 100nF; C0805
CIN, CIN1, CIN2: 10uF; C0805
COUT: 47uF; C0805
D2: 1N4148W; SOD-123_MINI-SMA
D3: NSR0320MW2T1G; SOD323_ST
D4, D5: SMAJ60A; DO_214
GND, GND1: TPPAD1-13; P1-13
I2C_3V, I2C_5V: DF51-4POS
J1: PJS008U-3000-0; CONN_PJS008U-3000-0_YAM
J2: MEM2051-00-195-00-A; GCT_MEM2051-00-195-00-A
L1: 10UH 2.7A; WE-MAPI_40XX
L3: LB3218T1R0M; INDC3218X200N
LED: 2.5MM_JST_UP_2POS; JST_2POS_2.5MM_UP
LED1: Yellow; CHIPLED_0805
LED2: RED; CHIPLED_0805
MS1: FEATHERWING
NMOS: FDMS86101; 8-POWERTDFN
PMOS1, PMOS2: DMP3099L-7; SOT-23-3
PMOS3: DMP3056LDM-7; SOT23-6
PRESSURE: DF51-4POS
PRESSURE_SENSOR: MS580302BA01-00; MS5803-02BA01
P_MOS: 130mA/20V; SOT23-3
Q1, Q2, Q3: DMN65D8L-7; SOT23-S
R1: 1M; R0805
R2: 300k; R0805
R3, R5, R9, R16, R17, R19, R20, R23: 10K; R0805
R4: 3k; R0805
R6, R18: 30k; RES_1206
R7, R8, R21: 100k; RES_1206
R10: 30K; R0805
R11: 6.2k; R0805
RGND: 1K; R0805
RTC: DS3231SNT&R; 21-0042B_16
SWITCH: 2MM_JST_PH_5POS; 2MM_5POS_HEADER
U$7: LTC4372; SOP65P640X120-8N
VREG: BUCK_REGULATORS; SOT23-6@1

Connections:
3V_MCU: MS1.2 (3V), PMOS2.S, R18.2, R23.1, SWITCH.5
5V_MCU: COUT.1, L1.2, MS1.26 (USB), PMOS1.S, R7.2, R11.2, VREG.3 (FB)
5V_SCL: I2C_5V.P$4 (P4), R20.2; also elsewhere on the board
5V_SDA: I2C_5V.P$3 (P3), R19.2; also elsewhere on the board
12V_IN: CIN1.1, CIN2.1, D4.C, D5.C, L3.1, NMOS.5 (D), NMOS.6 (D), NMOS.7 (D), NMOS.8 (D), NMOS.9 (D), PMOS3.4 (S), R8.2, U$7.1 (OUT)
+3V3: 0X76.2, 3V.TP, ANALOG1.P$1 (P1), ANALOG2.P$1 (P1), C14.1, C17.1, C18.1, I2C_3V.P$1 (P1), J1.4 (VDD), J2.4 (VDD), PMOS2.D, PRESSURE.P$1 (P1), PRESSURE_SENSOR.5 (VDD), PRESSURE_SENSOR.6 (PS), P_MOS.2 (S), R3.2, R5.2, R9.1, R16.1, R17.2, RTC.2 (VCC); also elsewhere on the board
+5V: 5V.TP, I2C_5V.P$1 (P1), PMOS1.D, R19.1, R20.1; also elsewhere on the board
+12V: 12V.TP, PMOS3.1 (D), PMOS3.2 (D), PMOS3.5 (D), PMOS3.6 (D), R1.2; also elsewhere on the board
+12V_NON_PROTECT: 12V_IN.PWR2 (TIP), D5.A, NMOS.1 (S), NMOS.2 (S), NMOS.3 (S), U$7.3 (SOURCE), U$7.4 (IN)
BATTERY_READ: C6.1, MS1.7 (GPIOA2), R1.1, R2.2
BUTTON1: BUTTON.2, MS1.25 (GPIO13), R23.2
CS: J1.2 (CD), J2.2 (DATA3/CD), MS1.22 (GPIO10)
DGND: 12V_IN.GND (RING), 12V_IN.GNDBREAK (RING_SW), ANALOG1.P$2 (P2), ANALOG2.P$2 (P2), B2.-, BUTTON.1, C3.2, C6.2, C14.2, C17.2, C18.2, CIN.2, CIN1.2, CIN2.2, COUT.2, D2.A, D4.A, GND.TP, GND1.TP, I2C_3V.P$2 (P2), I2C_5V.P$2 (P2), J1.6 (VSS), J2.6 (VSS), LED.1, LED1.C, LED2.C, MS1.4 (GND), PRESSURE.P$2 (P2), PRESSURE_SENSOR.2 (GND), Q1.2 (S), Q2.2 (S), Q3.2 (S), R2.1, R6.2, R10.2, RGND.1, RTC.5 (NC_2), RTC.6 (NC_3), RTC.7 (NC_4), RTC.8 (NC_5), RTC.9 (NC_6), RTC.10 (NC_7), RTC.11 (NC_8), RTC.12 (NC), RTC.13 (GND), SWITCH.4, VREG.2 (GND); also elsewhere on the board
DI: J1.3 (CMD), J2.3 (CMD), MS1.12 (GPIOMOSI)
DO: J1.7 (DAT0), J2.7 (DATA0), MS1.13 (GPIOMISO)
GND: D3.A
HB_IN1: MS1.20 (GPIO6); also elsewhere on the board
HB_IN2: MS1.19 (GPIO5); also elsewhere on the board
unnamed: B2.+, C3.1, RTC.14 (VBAT)
unnamed: P_MOS.3 (D), R4.2
unnamed: PMOS3.3 (G), Q2.3 (D), R8.1
unnamed: 0X76.1, PRESSURE_SENSOR.3 (CSB), R10.1
unnamed: NMOS.4 (G), U$7.2 (GATE)
unnamed: LED.2, LED1.A, R4.1
unnamed: PMOS1.G, Q1.3 (D), R7.1
unnamed: LED2.A, R11.1
unnamed: R21.1, VREG.4 (!SHDN)
unnamed: PMOS2.G, Q3.3 (D), R18.1
unnamed: CIN.1, L3.2, R21.2, VREG.5 (VIN)
unnamed: CBOOT.1, VREG.1 (CB)
unnamed: CBOOT.2, D3.C, L1.1, VREG.6 (SW)
unnamed: C5.1, U$7.5 (INTVCC)
unnamed: C5.2, D2.C, RGND.2, U$7.6 (GND), U$7.8 (SHDN)
RTC_INT: MS1.6 (GPIOA1), R17.1, RTC.3 (!INT/SQW), SWITCH.3
SCK: J1.5 (CLK), J2.5 (CLK), MS1.11 (GPIOSCK)
SCL: I2C_3V.P$4 (P4), MS1.18 (GPIOSCL), PRESSURE.P$4 (P4), PRESSURE_SENSOR.1 (SCLK), R3.1, RTC.16 (SCL); also elsewhere on the board
SDA: I2C_3V.P$3 (P3), MS1.17 (GPIOSDA), PRESSURE.P$3 (P3), PRESSURE_SENSOR.7 (SDI/SDA), R5.1, RTC.15 (SDA); also elsewhere on the board
SENSOR1: ANALOG1.P$3 (P3), MS1.8 (GPIOA3), R9.2
SENSOR2: ANALOG2.P$3 (P3), MS1.9 (GPIOA4), R16.2
SHIFT_CLK: MS1.23 (GPIO11); also elsewhere on the board
SHIFT_DATA: MS1.24 (GPIO12); also elsewhere on the board
SHIFT_LATCH: MS1.21 (GPIO9); also elsewhere on the board
SHUTDOWN: MS1.5 (GPIOA0), Q1.1 (G), Q2.1 (G), Q3.1 (G), R6.1
WAKE_NOSLEEP: MS1.10 (GPIOA5), P_MOS.1 (G), SWITCH.2

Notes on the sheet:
No Sleep LED
Feather M0 Wifi
To Sleep Switch
Input voltage ripple is 7.14mV
L > 6.8 uH, Imax > 1.6A
Default address is 0x77 unless solder jumper is bridged

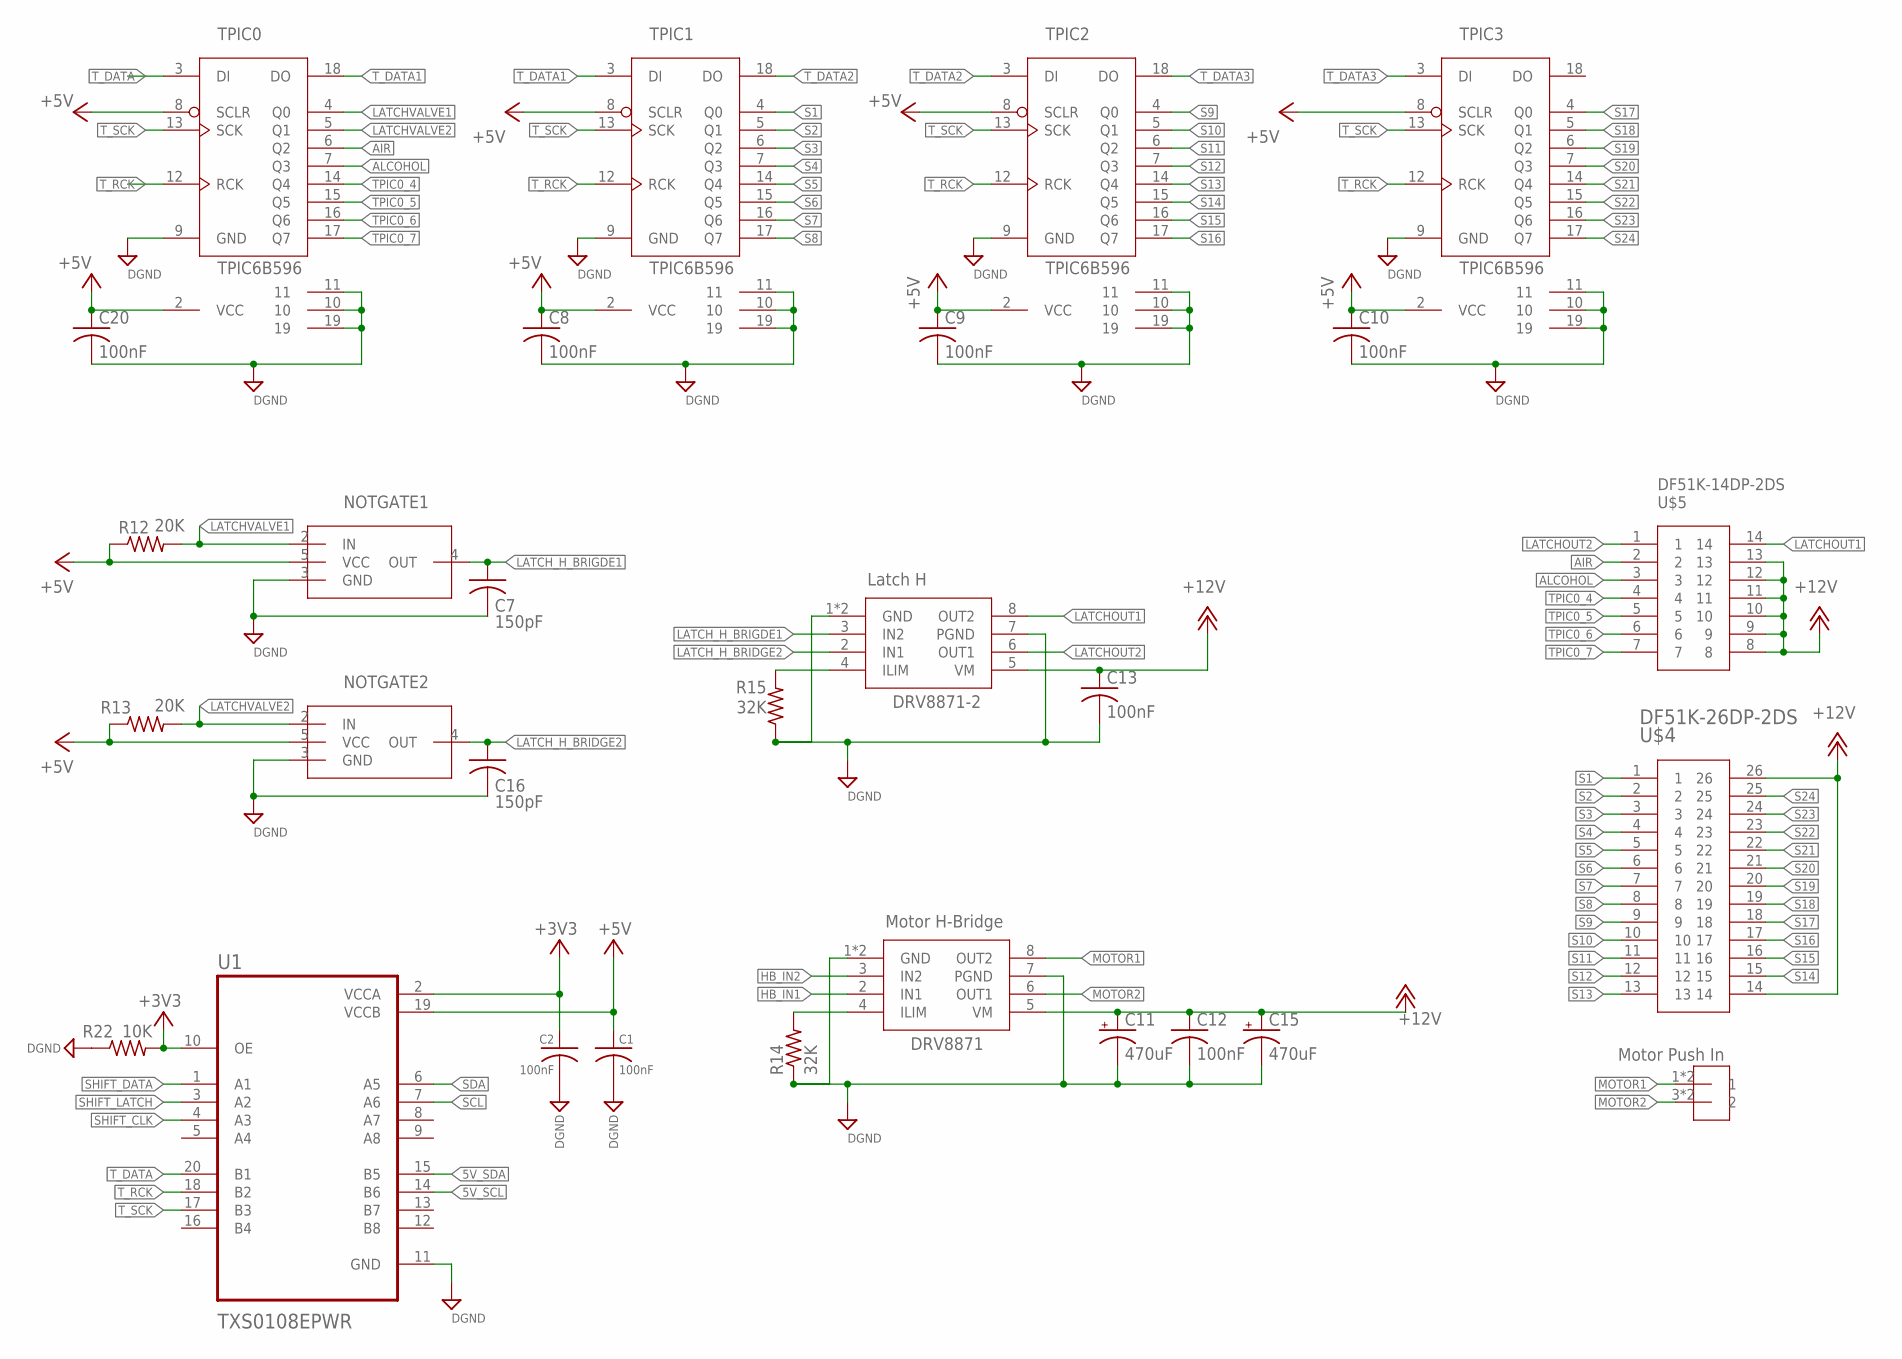
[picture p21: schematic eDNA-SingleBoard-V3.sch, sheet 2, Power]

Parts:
C1, C2, C8, C9, C10, C12, C13, C20: 100nF; C0805
C7, C16: 150pF; C0805
C11, C15: 470uF; 140CLH-0810
DRV8871: Motor H-Bridge; SOP8
DRV8871-2: Latch H; SOP8
NOTGATE1, NOTGATE2: NOT_GATE; SOT753
R12, R13: 20K; R0805
R14, R15: 32K; R0805
R22: 10K; R0805
TPIC0, TPIC1, TPIC2, TPIC3: TPIC6B596; DIP20
U1: TXS0108EPWR; SOP65P640X120-20N
U$2: Motor Push In; 3.5MM_DIP2
U$4: DF51K-26DP-2DS; DF51K-26DP-2DS-ANGLE
U$5: DF51K-14DP-2DS; DF51K-14DP-2DS-ANGLE

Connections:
5V_SCL: U1.14 (B6); also elsewhere on the board
5V_SDA: U1.15 (B5); also elsewhere on the board
+3V3: C2.1, R22.2, U1.2 (VCCA), U1.10 (OE); also elsewhere on the board
+5V: C1.1, C8.1, C9.1, C10.1, C20.1, NOTGATE1.5 (VCC), NOTGATE2.5 (VCC), R12.1, R13.1, TPIC0.2 (VCC), TPIC0.8 (SCLR), TPIC1.2 (VCC), TPIC1.8 (SCLR), TPIC2.2 (VCC), TPIC2.8 (SCLR), TPIC3.2 (VCC), TPIC3.8 (SCLR), U1.19 (VCCB); also elsewhere on the board
+12V: C11.+, C12.1, C13.1, C15.+, DRV8871.5 (VM), DRV8871-2.5 (VM), U$4.14, U$4.26, U$5.8, U$5.9, U$5.10, U$5.11, U$5.12, U$5.13; also elsewhere on the board
AIR: TPIC0.6 (Q2), U$5.2
ALCOHOL: TPIC0.7 (Q3), U$5.3
DGND: C1.2, C2.2, C7.2, C8.2, C9.2, C10.2, C11.-, C12.2, C13.2, C15.-, C16.2, C20.2, DRV8871.1 (GND), DRV8871.7 (PGND), DRV8871.GND, DRV8871-2.1 (GND), DRV8871-2.7 (PGND), DRV8871-2.GND, NOTGATE1.3 (GND), NOTGATE2.3 (GND), R14.1, R15.1, R22.1, TPIC0.9 (GND), TPIC0.10, TPIC0.11, TPIC0.19, TPIC1.9 (GND), TPIC1.10, TPIC1.11, TPIC1.19, TPIC2.9 (GND), TPIC2.10, TPIC2.11, TPIC2.19, TPIC3.9 (GND), TPIC3.10, TPIC3.11, TPIC3.19, U1.11 (GND); also elsewhere on the board
HB_IN1: DRV8871.2 (IN1); also elsewhere on the board
HB_IN2: DRV8871.3 (IN2); also elsewhere on the board
LATCHOUT1: DRV8871-2.8 (OUT2), U$5.14
LATCHOUT2: DRV8871-2.6 (OUT1), U$5.1
LATCHVALVE1: NOTGATE1.2 (IN), R12.2, TPIC0.4 (Q0)
LATCHVALVE2: NOTGATE2.2 (IN), R13.2, TPIC0.5 (Q1)
LATCH_H_BRIDGE2: C16.1, DRV8871-2.2 (IN1), NOTGATE2.4 (OUT)
LATCH_H_BRIGDE1: C7.1, DRV8871-2.3 (IN2), NOTGATE1.4 (OUT)
MOTOR1: DRV8871.8 (OUT2), U$2.1, U$2.2 (1)
MOTOR2: DRV8871.6 (OUT1), U$2.3 (2), U$2.4 (2)
unnamed: DRV8871.4 (ILIM), R14.2
unnamed: DRV8871-2.4 (ILIM), R15.2
S1: TPIC1.4 (Q0), U$4.1
S2: TPIC1.5 (Q1), U$4.2
S3: TPIC1.6 (Q2), U$4.3
S4: TPIC1.7 (Q3), U$4.4
S5: TPIC1.14 (Q4), U$4.5
S6: TPIC1.15 (Q5), U$4.6
S7: TPIC1.16 (Q6), U$4.7
S8: TPIC1.17 (Q7), U$4.8
S9: TPIC2.4 (Q0), U$4.9
S10: TPIC2.5 (Q1), U$4.10
S11: TPIC2.6 (Q2), U$4.11
S12: TPIC2.7 (Q3), U$4.12
S13: TPIC2.14 (Q4), U$4.13
S14: TPIC2.15 (Q5), U$4.15
S15: TPIC2.16 (Q6), U$4.16
S16: TPIC2.17 (Q7), U$4.17
S17: TPIC3.4 (Q0), U$4.18
S18: TPIC3.5 (Q1), U$4.19
S19: TPIC3.6 (Q2), U$4.20
S20: TPIC3.7 (Q3), U$4.21
S21: TPIC3.14 (Q4), U$4.22
S22: TPIC3.15 (Q5), U$4.23
S23: TPIC3.16 (Q6), U$4.24
S24: TPIC3.17 (Q7), U$4.25
SCL: U1.7 (A6); also elsewhere on the board
SDA: U1.6 (A5); also elsewhere on the board
SHIFT_CLK: U1.4 (A3); also elsewhere on the board
SHIFT_DATA: U1.1 (A1); also elsewhere on the board
SHIFT_LATCH: U1.3 (A2); also elsewhere on the board
TPIC0_4: TPIC0.14 (Q4), U$5.4
TPIC0_5: TPIC0.15 (Q5), U$5.5
TPIC0_6: TPIC0.16 (Q6), U$5.6
TPIC0_7: TPIC0.17 (Q7), U$5.7
T_DATA: TPIC0.3 (DI), U1.20 (B1)
T_DATA1: TPIC0.18 (DO), TPIC1.3 (DI)
T_DATA2: TPIC1.18 (DO), TPIC2.3 (DI)
T_DATA3: TPIC2.18 (DO), TPIC3.3 (DI)
T_RCK: TPIC0.12 (RCK), TPIC1.12 (RCK), TPIC2.12 (RCK), TPIC3.12 (RCK), U1.18 (B2)
T_SCK: TPIC0.13 (SCK), TPIC1.13 (SCK), TPIC2.13 (SCK), TPIC3.13 (SCK), U1.17 (B3)

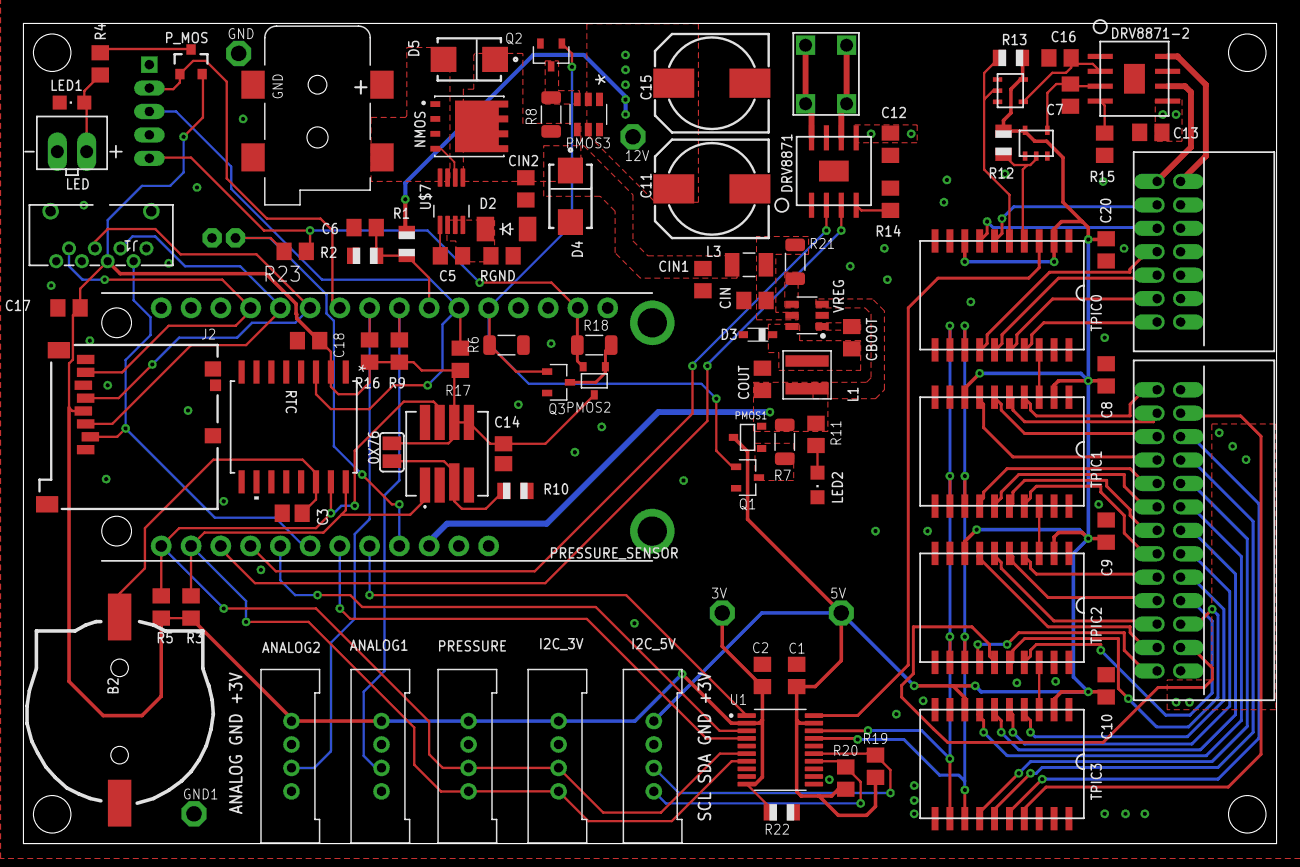
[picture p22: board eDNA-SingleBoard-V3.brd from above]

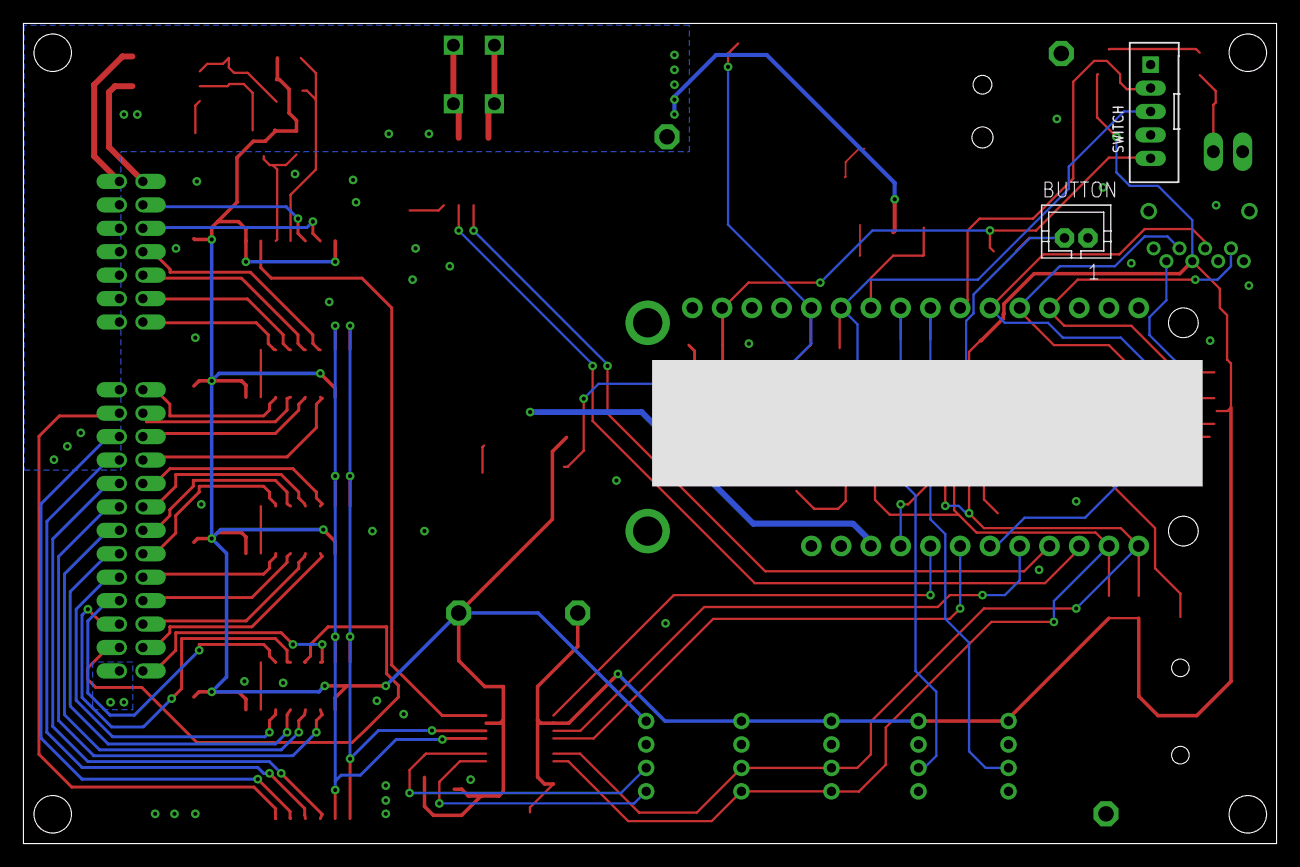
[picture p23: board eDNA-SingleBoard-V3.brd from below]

Board: 2 copper layers, 107.0 x 70.0 mm, 98 parts (2 on the bottom side), 89 nets.

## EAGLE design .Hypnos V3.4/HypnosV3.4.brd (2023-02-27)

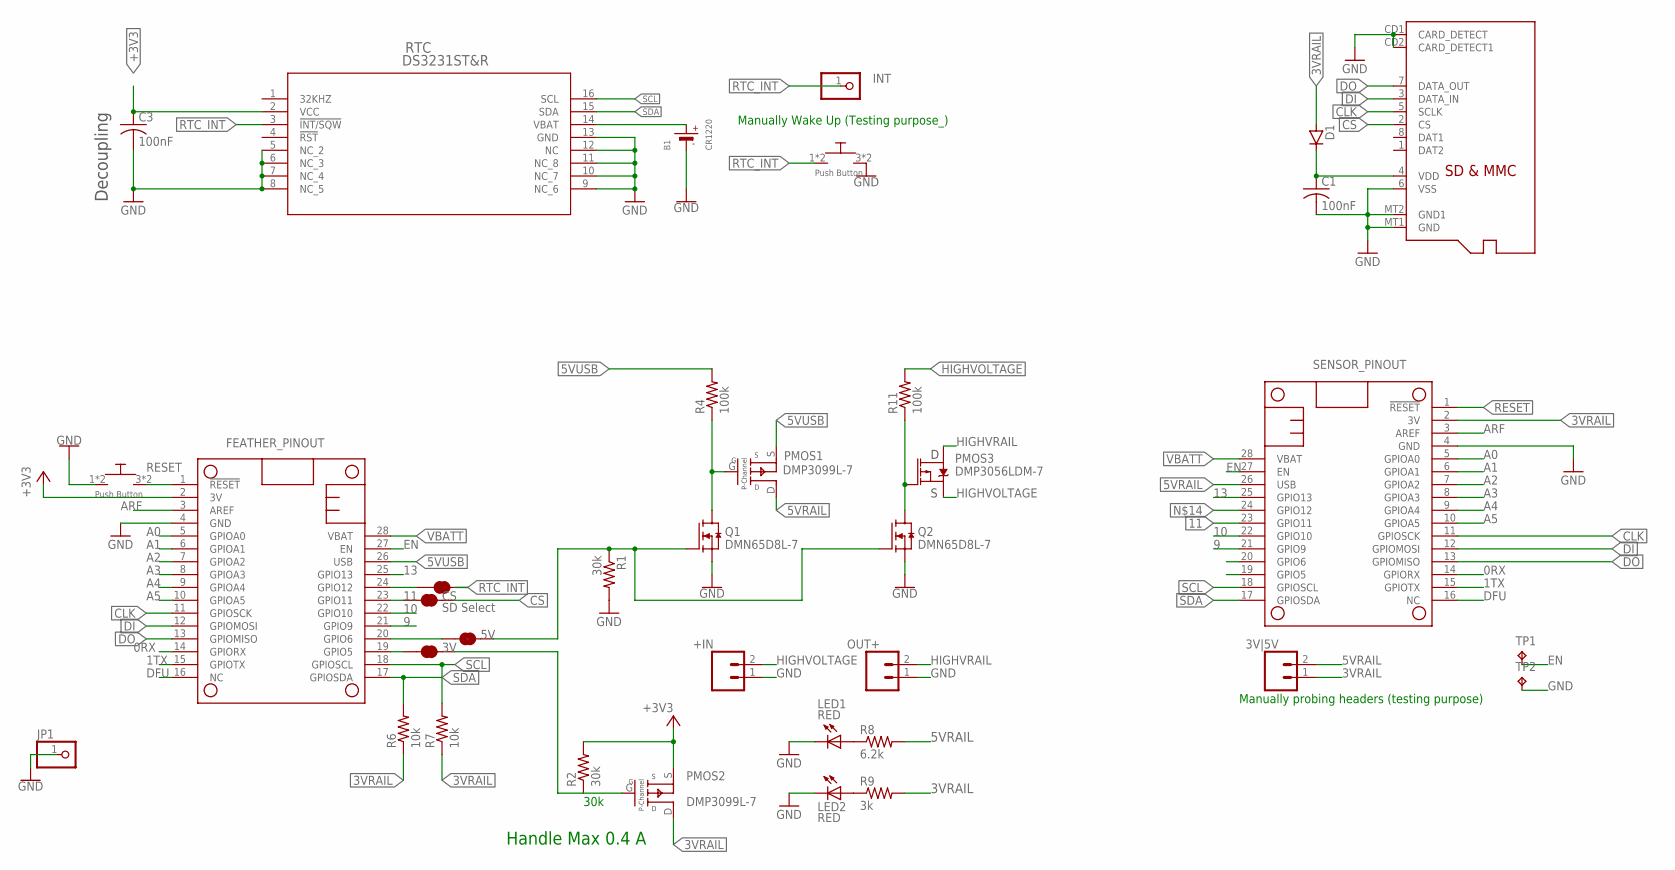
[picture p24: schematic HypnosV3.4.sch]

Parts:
3V, 5V: JUMPER-SMT_2_NC_TRACE_SILK; SMT-JUMPER_2_NC_TRACE_SILK
3V|5V: CONN_021X02_NO_SILK; 1X02_NO_SILK
+IN: HIGHV-IN; 1X02_NO_SILK
B1: CR1220
C1, C3: 100nF; C1206
CS: SD Select; SMT-JUMPER_2_NC_TRACE_SILK
D1: D-SOD123; SOD123
FEATHERWING: SENSOR_PINOUT; FEATHERWING
INT: PINHD-1X1CB; 1X01-CLEANBIG
JP1: PINHD-1X1CB; 1X01-CLEANBIG
LED1, LED2: RED; CHIPLED_0805
MICROSD: MICROSD
MS2: FEATHER_PINOUT; FEATHERWING
OUT+: HIGHV-OUT; 1X02_NO_SILK
PMOS1, PMOS2: DMP3099L-7; SOT-23-3
PMOS3: DMP3056LDM-7; SOT23-6
Q1, Q2: DMN65D8L-7; SOT23-S
R1, R2: 30k; RES_1206
R4, R11: 100k; RES_1206
R6, R7: 10k; RES_1206
R8: 6.2k; RES_1206
R9: 3k; RES_1206
RTC: DS3231ST&R; 21-0042B_16
RTC_INT: JUMPER-SMT_2_NC_TRACE_SILK; SMT-JUMPER_2_NC_TRACE_SILK
TP1, TP2: TPTP16R; TP16R
U$1, U$2: PUSH_BUTTON; PUSHBUTTON_SMD

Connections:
0RX: FEATHERWING.14 (GPIORX), MS2.14 (GPIORX)
1TX: FEATHERWING.15 (GPIOTX), MS2.15 (GPIOTX)
3VRAIL: 3V|5V.1, D1.2 (A), FEATHERWING.2 (3V), PMOS2.D, R6.1, R7.1, R9.2
5VRAIL: 3V|5V.2, FEATHERWING.26 (USB), PMOS1.D, R8.2
5VUSB: MS2.26 (USB), PMOS1.S, R4.2
9: FEATHERWING.21 (GPIO9), MS2.21 (GPIO9)
10: FEATHERWING.22 (GPIO10), MS2.22 (GPIO10)
11: CS.1, FEATHERWING.23 (GPIO11), MS2.23 (GPIO11)
13: FEATHERWING.25 (GPIO13), MS2.25 (GPIO13)
+3V3: C3.1, MS2.2 (3V), PMOS2.S, R2.2, RTC.2 (VCC)
A0: FEATHERWING.5 (GPIOA0), MS2.5 (GPIOA0)
A1: FEATHERWING.6 (GPIOA1), MS2.6 (GPIOA1)
A2: FEATHERWING.7 (GPIOA2), MS2.7 (GPIOA2)
A3: FEATHERWING.8 (GPIOA3), MS2.8 (GPIOA3)
A4: FEATHERWING.9 (GPIOA4), MS2.9 (GPIOA4)
A5: FEATHERWING.10 (GPIOA5), MS2.10 (GPIOA5)
ARF: FEATHERWING.3 (AREF), MS2.3 (AREF)
CLK: FEATHERWING.11 (GPIOSCK), MICROSD.5 (SCLK), MS2.11 (GPIOSCK)
CS: CS.2, MICROSD.2 (CS)
DFU: FEATHERWING.16 (NC), MS2.16 (NC)
DI: FEATHERWING.12 (GPIOMOSI), MICROSD.3 (DATA_IN), MS2.12 (GPIOMOSI)
DO: FEATHERWING.13 (GPIOMISO), MICROSD.7 (DATA_OUT), MS2.13 (GPIOMISO)
EN: FEATHERWING.27 (EN), MS2.27 (EN), TP1.TP
GND: +IN.1, B1.-, C1.2, C3.2, FEATHERWING.4 (GND), JP1.1, LED1.C, LED2.C, MICROSD.6 (VSS), MICROSD.CD1 (CARD_DETECT), MICROSD.CD2 (CARD_DETECT1), MICROSD.MT1 (GND), MICROSD.MT2 (GND1), MS2.4 (GND), OUT+.1, Q1.2 (S), Q2.2 (S), R1.2, RTC.5 (NC_2), RTC.6 (NC_3), RTC.7 (NC_4), RTC.8 (NC_5), RTC.9 (NC_6), RTC.10 (NC_7), RTC.11 (NC_8), RTC.12 (NC), RTC.13 (GND), TP2.TP, U$1.1, U$1.2, U$2.3, U$2.4
HIGHVOLTAGE: +IN.2, PMOS3.4 (S), R11.2
HIGHVRAIL: OUT+.2, PMOS3.1 (D), PMOS3.2 (D), PMOS3.5 (D), PMOS3.6 (D)
unnamed: 5V.1, MS2.20 (GPIO6)
unnamed: B1.+$1 (+), RTC.14 (VBAT)
unnamed: 3V.1, MS2.19 (GPIO5)
unnamed: 5V.2, Q1.1 (G), Q2.1 (G), R1.1
unnamed: 3V.2, PMOS2.G, R2.1
unnamed: PMOS1.G, Q1.3 (D), R4.1
unnamed: LED1.A, R8.1
unnamed: LED2.A, R9.1
unnamed: FEATHERWING.24 (GPIO12), MS2.24 (GPIO12), RTC_INT.1
unnamed: PMOS3.3 (G), Q2.3 (D), R11.1
RESET: FEATHERWING.1 (!RESET), MS2.1 (!RESET), U$1.3, U$1.4
RTC_INT: INT.1, RTC.3 (!INT/SQW), RTC_INT.2, U$2.1, U$2.2
SCL: FEATHERWING.18 (GPIOSCL), MS2.18 (GPIOSCL), R7.2, RTC.16 (SCL)
SDA: FEATHERWING.17 (GPIOSDA), MS2.17 (GPIOSDA), R6.2, RTC.15 (SDA)
VBATT: FEATHERWING.28 (VBAT), MS2.28 (VBAT)
VDD: C1.1, D1.1 (C), MICROSD.4 (VDD)

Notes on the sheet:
Decoupling
Manually Wake Up (Testing purpose_)
Manually probing headers (testing purpose)
30k
Handle Max 0.4 A

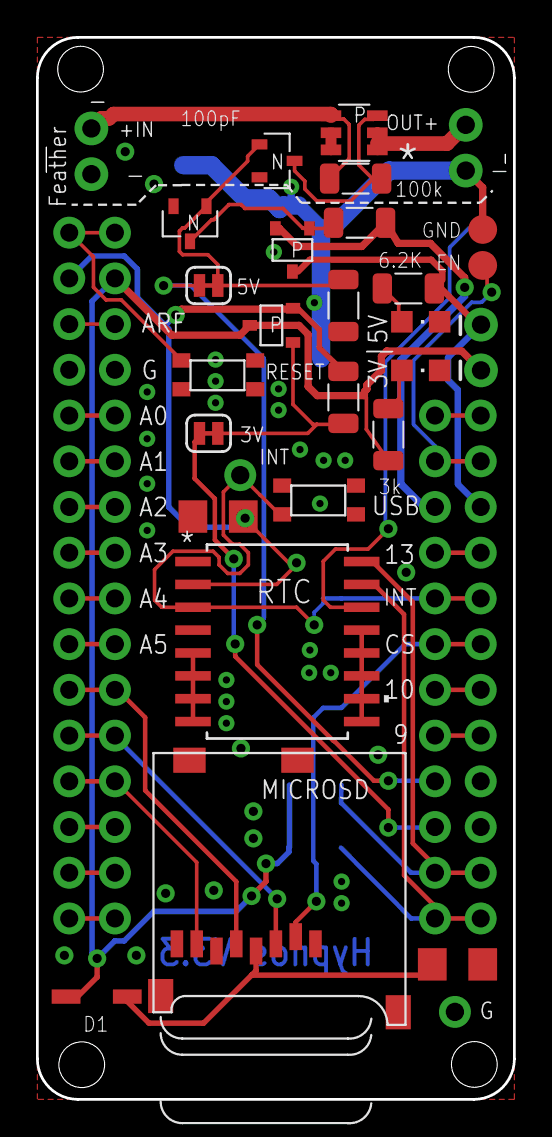
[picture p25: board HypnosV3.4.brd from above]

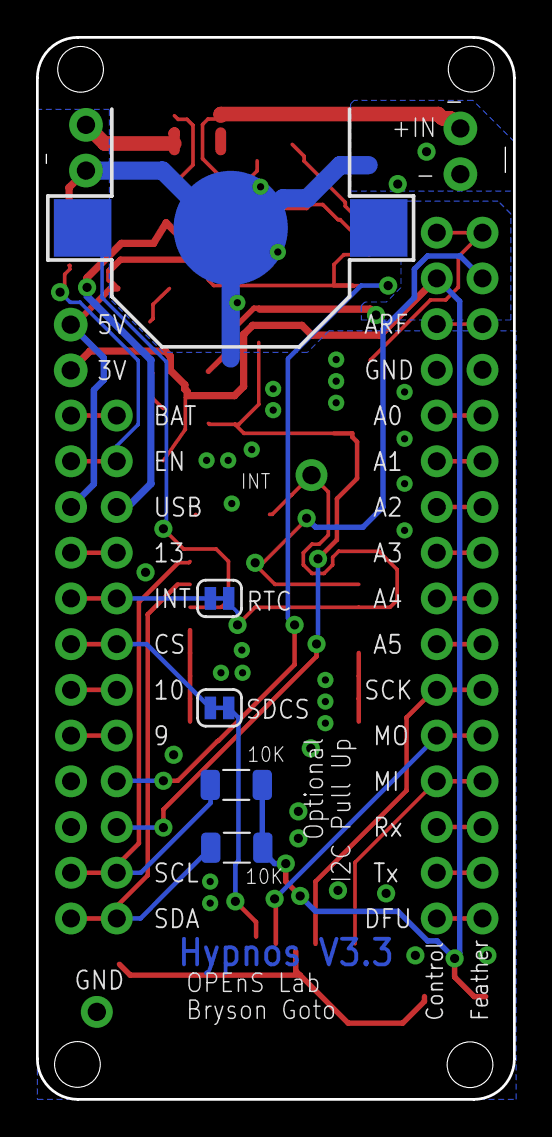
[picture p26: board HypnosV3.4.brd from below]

Board: 2 copper layers, 26.5 x 59.0 mm, 36 parts (6 on the bottom side), 42 nets.

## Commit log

2023-02-16 Added Existing Files
    [eDNA-SingleBoard-V1.brd, eDNA-SingleBoard-V1.sch]
2023-02-26 Renamed the files
    [eDNA-SingleBoard-V3.brd, eDNA-SingleBoard-V3.sch]
2023-02-27 Updated the SCH and PCB Files
    Nearly completed the update to the Schematic.
    Started to ripup all the traces on the PCB
    [HypnosV3.4.brd, HypnosV3.4.sch]
2023-02-27 Updated Schematic
    [eDNA-SingleBoard-V3.sch]
2023-03-01 Updated Schematic and PCB Files
    [eDNA-SingleBoard-V3.sch]
2023-03-02 Updated SCH and PCB
    [eDNA-SingleBoard-V3.brd, eDNA-SingleBoard-V3.sch]
2023-03-03 Update the PCB
2023-03-06 Added External Interrupt
    [eDNA-SingleBoard-V3.brd]
2023-03-06 Added Silkscreen area for serial number
    [eDNA-SingleBoard-V3.brd]
2023-03-11 Added Gerber Files
    [PnP_eDNA-SingleBoard-V3_front.csv, copper_bottom.gbr, copper_top.gbr, drill_1_16.xln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]
2023-04-09 Removed Unnecessary Backup Files
    [HypnosV3.4.brd, HypnosV3.4.sch, eDNA-SingleBoard-V3.brd, eDNA-SingleBoard-V3.sch]

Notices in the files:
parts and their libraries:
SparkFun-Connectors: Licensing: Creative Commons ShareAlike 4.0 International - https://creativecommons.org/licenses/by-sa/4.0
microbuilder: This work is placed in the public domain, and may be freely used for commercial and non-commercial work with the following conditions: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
